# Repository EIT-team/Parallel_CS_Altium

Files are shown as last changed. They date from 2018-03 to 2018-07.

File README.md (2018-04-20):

# Parallel_CS_Altium

Altium files (root directory), fabrcation/assembly data and source code for UCL Parallel EIT Current Source.

### Fabrication_and_Assembly_Files
The most recently used Gerber files, BOM and Pick and Place data are included.

### src
Arduino source code for programming the CS. The latest board uses a 3.3V Arduino Pro Mini (ATMega328P).

### doc
Contains Circuit description, assembly instructions and operating instructions.

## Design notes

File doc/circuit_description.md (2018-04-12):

## Top level schematic
The design uses Altium's hierarchical sheet setup to replicate the CS block six times.
Additional sheets are used for the Power Supply/USB/Buttons and for the Arduino connector and clock source
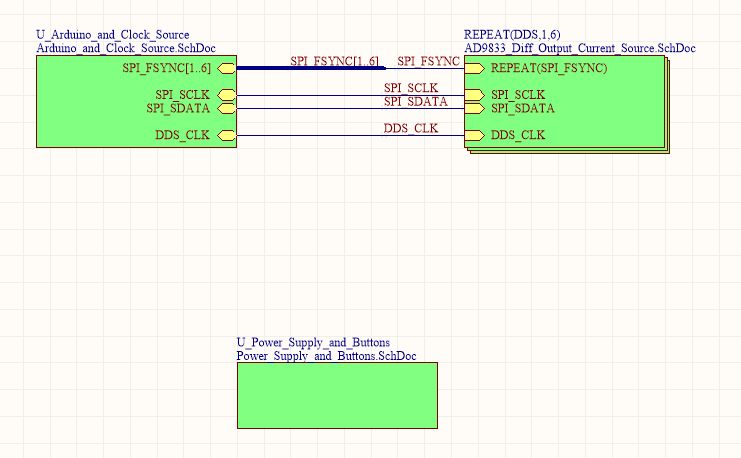
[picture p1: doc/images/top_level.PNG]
TOP


## Arduino Connector
A footprint for an Arduino Pro Micro/Pro Mini is included, which is used for sending SPI signals to the DDS chips. Each of the six current sources has its own FSYNC line.
The Arduino will need to be programmed once using the Arduino IDE, after which the frequencies are stored on board and it can be powered by the batery input.
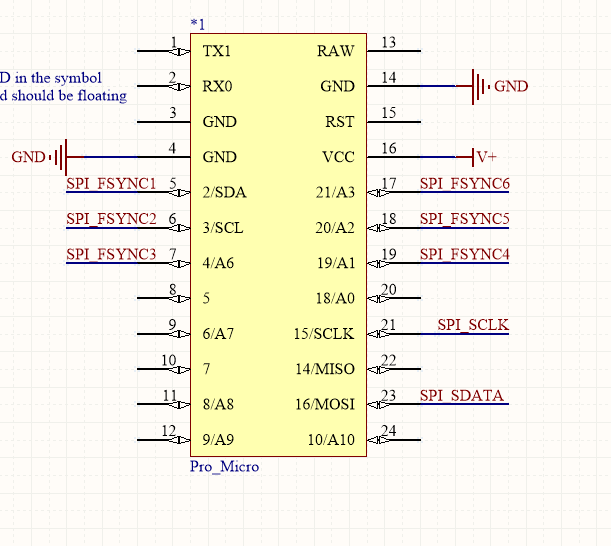
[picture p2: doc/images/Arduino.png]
ARDUINO


## Clock source
LTC6900 is used to generate a 10MHz clock signal for the DDS chips.  The clock speed is set by the resitor R17.
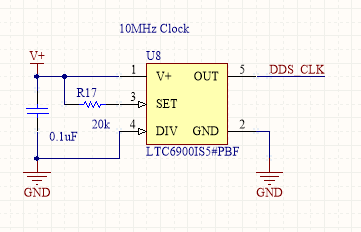
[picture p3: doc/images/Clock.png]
CLOCK


##Negate voltage generator
The op amps used in the single ended to differential convertor and the Howland Current Pump require a negative voltage. The LTC1044 generates this, from either the battery input or the USB line.
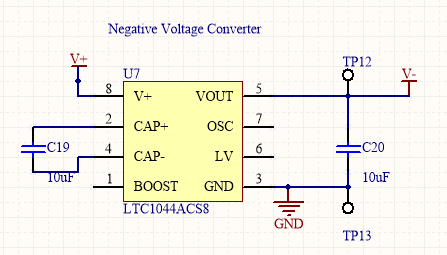
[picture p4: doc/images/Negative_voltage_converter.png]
VOLTAGE


## Battery and USB charger
Power can be supplied to the cirucit (including the Arduino) from a battery, or from the USB line. Switch S1 connects the battery, powering up the circuits. The on board LiPo charger can be used to charge the battery over USB.
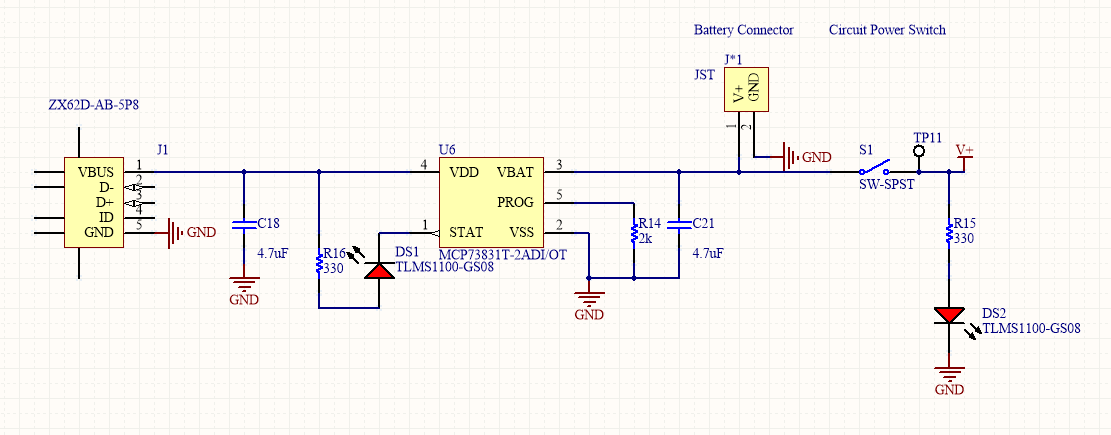
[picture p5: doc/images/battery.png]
BATTERY


## DDS and analog filter
AD9833 generates a 10-bit sine wave with 0.6V amplitude, the frequency is programmed over SPI from the Arduino. Op-amps U3A/U3B impement an image filter to reduce the higher frequency components on the sharp edges of the DDS signal.
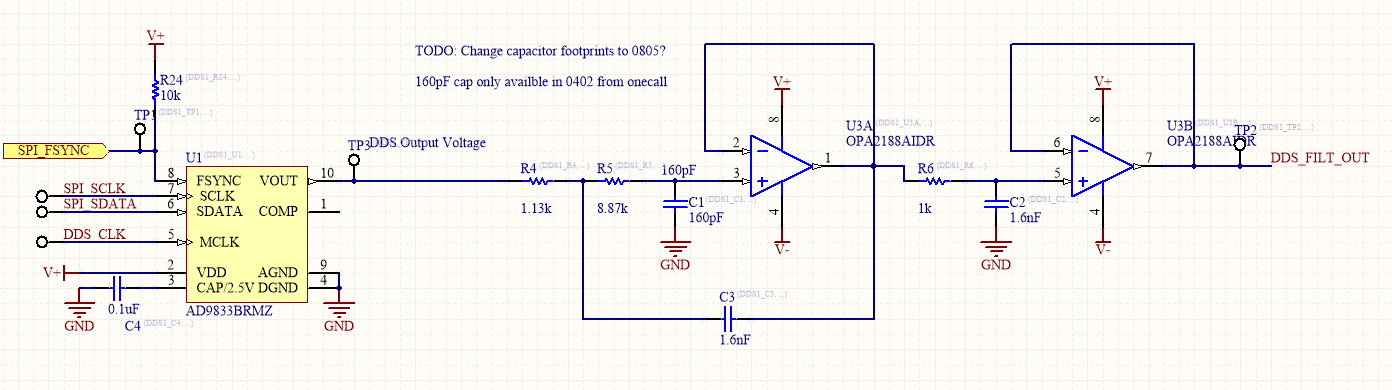
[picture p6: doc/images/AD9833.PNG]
DDS


## Single ended to differential conversion
The signal from the DDS/Filter block is single ended (reference to ground), but for parallel injection, differential signals are needed. These can be generated _either_ by the U9A/U9B op amp configuraiton _or_ the AD8476 IC. The AD8476 is a more expensive compoent, but is a simpler solution.
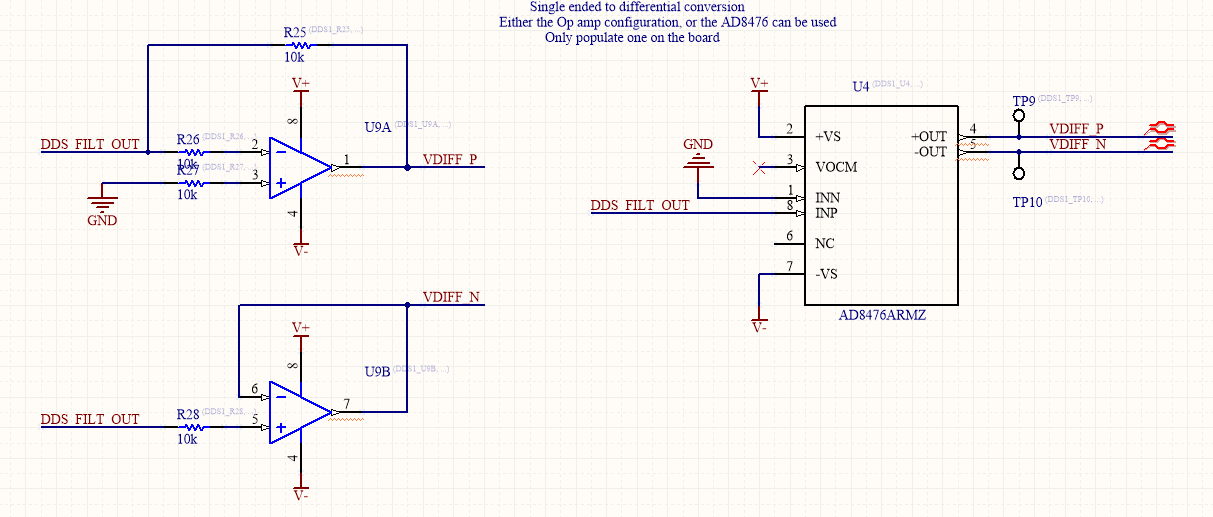
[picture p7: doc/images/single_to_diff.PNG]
DIFF


## Howland Current Pump
A differntial input Improved HCP circuit converts the DDS voltage signal to an output current. 4 output resistors are included to allow for selection of the output current, by using the header connections P2/P3 (both headers should be set to the same value).

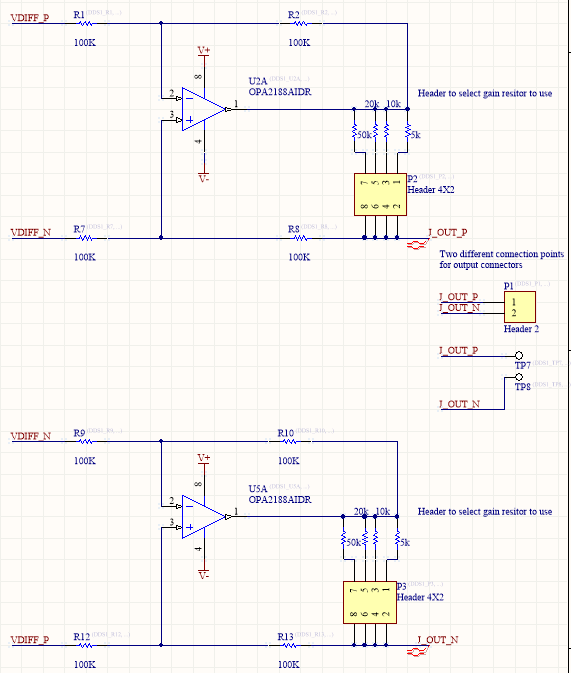
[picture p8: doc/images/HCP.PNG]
HCP


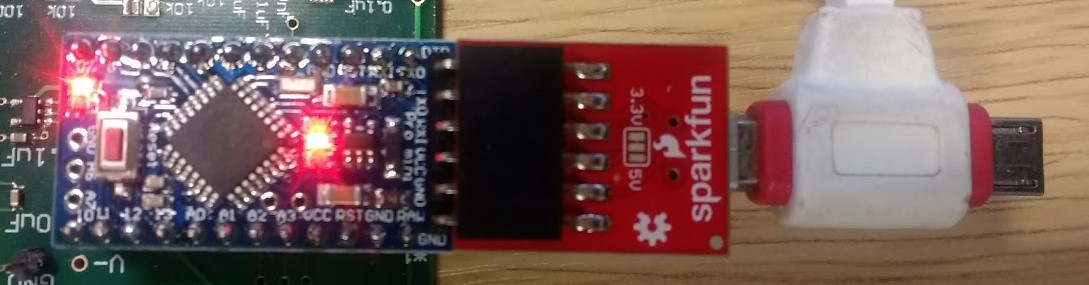
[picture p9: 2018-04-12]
doc/images/arduino-connected.jpg

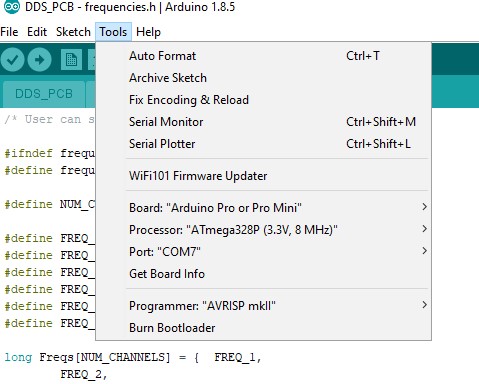
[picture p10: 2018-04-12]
doc/images/arduino-settings.jpg

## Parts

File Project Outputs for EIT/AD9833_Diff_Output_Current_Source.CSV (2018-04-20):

Bill of Material for
On 20/04/2018 at 06:43:15
Comment | Pattern | Quantity | Components
0.1uF | 1608[0603] | 73 | C22, DDS1_C4, DDS1_C5, DDS1_C6, DDS1_C7, DDS1_C8, DDS1_C9, DDS1_C10, DDS1_C12, DDS1_C14, DDS1_C16, DDS1_C23, DDS1_C24, DDS2_C4, DDS2_C5, DDS2_C6, DDS2_C7, DDS2_C8, DDS2_C9, DDS2_C10, DDS2_C12, DDS2_C14, DDS2_C16, DDS2_C23, DDS2_C24, DDS3_C4, DDS3_C5, DDS3_C6, DDS3_C7, DDS3_C8, DDS3_C9, DDS3_C10, DDS3_C12, DDS3_C14, DDS3_C16, DDS3_C23, DDS3_C24, DDS4_C4, DDS4_C5, DDS4_C6, DDS4_C7, DDS4_C8, DDS4_C9, DDS4_C10, DDS4_C12, DDS4_C14, DDS4_C16, DDS4_C23, DDS4_C24, DDS5_C4, DDS5_C5, DDS5_C6, DDS5_C7, DDS5_C8, DDS5_C9, DDS5_C10, DDS5_C12, DDS5_C14, DDS5_C16, DDS5_C23, DDS5_C24, DDS6_C4, DDS6_C5, DDS6_C6, DDS6_C7, DDS6_C8, DDS6_C9, DDS6_C10, DDS6_C12, DDS6_C14, DDS6_C16, DDS6_C23, DDS6_C24 | Capacitor (Semiconductor SIM Model)
100K | 6-0805_M | 48 | DDS1_R1, DDS1_R2, DDS1_R7, DDS1_R8, DDS1_R9, DDS1_R10, DDS1_R12, DDS1_R13, DDS2_R1, DDS2_R2, DDS2_R7, DDS2_R8, DDS2_R9, DDS2_R10, DDS2_R12, DDS2_R13, DDS3_R1, DDS3_R2, DDS3_R7, DDS3_R8, DDS3_R9, DDS3_R10, DDS3_R12, DDS3_R13, DDS4_R1, DDS4_R2, DDS4_R7, DDS4_R8, DDS4_R9, DDS4_R10, DDS4_R12, DDS4_R13, DDS5_R1, DDS5_R2, DDS5_R7, DDS5_R8, DDS5_R9, DDS5_R10, DDS5_R12, DDS5_R13, DDS6_R1, DDS6_R2, DDS6_R7, DDS6_R8, DDS6_R9, DDS6_R10, DDS6_R12, DDS6_R13 | Resistor
10k | 6-0805_M | 48 | DDS1_R6, DDS1_R18, DDS1_R21, DDS1_R24, DDS1_R25, DDS1_R26, DDS1_R27, DDS1_R28, DDS2_R6, DDS2_R18, DDS2_R21, DDS2_R24, DDS2_R25, DDS2_R26, DDS2_R27, DDS2_R28, DDS3_R6, DDS3_R18, DDS3_R21, DDS3_R24, DDS3_R25, DDS3_R26, DDS3_R27, DDS3_R28, DDS4_R6, DDS4_R18, DDS4_R21, DDS4_R24, DDS4_R25, DDS4_R26, DDS4_R27, DDS4_R28, DDS5_R6, DDS5_R18, DDS5_R21, DDS5_R24, DDS5_R25, DDS5_R26, DDS5_R27, DDS5_R28, DDS6_R6, DDS6_R18, DDS6_R21, DDS6_R24, DDS6_R25, DDS6_R26, DDS6_R27, DDS6_R28 | Resistor
10nF | 1608[0603] | 6 | DDS1_C11, DDS2_C11, DDS3_C11, DDS4_C11, DDS5_C11, DDS6_C11 | Capacitor (Semiconductor SIM Model)
10uF | 1608[0603] | 20 | C19, C20, DDS1_C13, DDS1_C15, DDS1_C17, DDS2_C13, DDS2_C15, DDS2_C17, DDS3_C13, DDS3_C15, DDS3_C17, DDS4_C13, DDS4_C15, DDS4_C17, DDS5_C13, DDS5_C15, DDS5_C17, DDS6_C13, DDS6_C15, DDS6_C17 | Capacitor (Semiconductor SIM Model)
13k | 6-0805_M | 6 | DDS1_R5, DDS2_R5, DDS3_R5, DDS4_R5, DDS5_R5, DDS6_R5 | Resistor
1u | 1608[0603] | 6 | DDS1_C2, DDS2_C2, DDS3_C2, DDS4_C2, DDS5_C2, DDS6_C2 | Capacitor (Semiconductor SIM Model)
2.2nF | 1608[0603] | 6 | DDS1_C3, DDS2_C3, DDS3_C3, DDS4_C3, DDS5_C3, DDS6_C3 | Capacitor (Semiconductor SIM Model)
20k | 6-0805_M | 13 | DDS1_R11, DDS1_R22, DDS2_R11, DDS2_R22, DDS3_R11, DDS3_R22, DDS4_R11, DDS4_R22, DDS5_R11, DDS5_R22, DDS6_R11, DDS6_R22, R17 | Resistor
220pF | 1608[0603] | 6 | DDS1_C1, DDS2_C1, DDS3_C1, DDS4_C1, DDS5_C1, DDS6_C1 | Capacitor (Semiconductor SIM Model)
2k | 6-0805_M | 1 | R14 | Resistor
330 | 6-0805_M | 2 | R15, R16 | Resistor
4.7uF | 1608[0603] | 2 | C18, C21 | Capacitor (Semiconductor SIM Model)
50k | 6-0805_M | 12 | DDS1_R3, DDS1_R23, DDS2_R3, DDS2_R23, DDS3_R3, DDS3_R23, DDS4_R3, DDS4_R23, DDS5_R3, DDS5_R23, DDS6_R3, DDS6_R23 | Resistor
5k | 6-0805_M | 12 | DDS1_R19, DDS1_R20, DDS2_R19, DDS2_R20, DDS3_R19, DDS3_R20, DDS4_R19, DDS4_R20, DDS5_R19, DDS5_R20, DDS6_R19, DDS6_R20 | Resistor
715 | 6-0805_M | 6 | DDS1_R4, DDS2_R4, DDS3_R4, DDS4_R4, DDS5_R4, DDS6_R4 | Resistor
AD8476ARMZ | SOP65P490X110-8N | 6 | DDS1_U4, DDS2_U4, DDS3_U4, DDS4_U4, DDS5_U4, DDS6_U4 | SP Amp DIFF AMP Single R-R O/P Â±9V/18V 8-Pin MSOP Tube
AD9833BRMZ | ADI-RM-10_M | 6 | DDS1_U1, DDS2_U1, DDS3_U1, DDS4_U1, DDS5_U1, DDS6_U1 | Low Power, 12.65 mW, 2.3 V to 5.5 V, Programmable Waveform Generator, 10-Bit, Serial, RM-10, 50 Tube, Pb-Free
Header 2 | HDR1X2 | 6 | DDS1_P1, DDS2_P1, DDS3_P1, DDS4_P1, DDS5_P1, DDS6_P1 | Header, 2-Pin
Header 4X2 | HDR2X4 | 12 | DDS1_P2, DDS1_P3, DDS2_P2, DDS2_P3, DDS3_P2, DDS3_P3, DDS4_P2, DDS4_P3, DDS5_P2, DDS5_P3, DDS6_P2, DDS6_P3 | Header, 4-Pin, Dual row
JST | JST- S2B-PH-SM4-TB(LF)(SN)-2_V | 1 | J*1
LTC1044ACS8 | LT-S8-8_M | 1 | U7 | 12 V CMOS Voltage Converter, 8-pin SOIC (S8-8), 0 to 70 degC
LTC6900IS5#PBF | LT-TSOT-23-5_V | 1 | U8 | Low Power, Resistor Set Oscillator, 1 KHz to 20 MHz, 2.7 to 5.5 V, -40 to 85 degC, 5-Pin SOT-23 (S5), Pb-Free
MCP73831T-2ADI/OT | SOT-23-OT5_M | 1 | U6 | Miniature Single-Cell, Fully Integrated Li-Ion, Li-Polymer Charge Management Controller, 4.2V, 5-Pin SOT-23, Industrial Temperature, Tape and Reel
OPA2188AIDR | D0008A_L | 24 | DDS1_U2, DDS1_U3, DDS1_U5, DDS1_U9, DDS2_U2, DDS2_U3, DDS2_U5, DDS2_U9, DDS3_U2, DDS3_U3, DDS3_U5, DDS3_U9, DDS4_U2, DDS4_U3, DDS4_U5, DDS4_U9, DDS5_U2, DDS5_U3, DDS5_U5, DDS5_U9, DDS6_U2, DDS6_U3, DDS6_U5, DDS6_U9 | 0.03 uV/degC, 6 uV Vos, Low Noise, Rail-to-Rail Output, Zero-Drift Operational Amplifier, 4 to 36 V, -40 to 105 degC, 8-pin SOIC (D8), Green (RoHS & no Sb/Br)
Pro_Micro | Pro_Micro | 1 | *1
SW-SPST | SPST-2 | 1 | S1 | Single-Pole, Single-Throw Switch
TESTPOINT_WHITE | TestPointVia | 63 | DDS1_TP1, DDS1_TP2, DDS1_TP3, DDS1_TP4, DDS1_TP5, DDS1_TP6, DDS1_TP7, DDS1_TP8, DDS1_TP9, DDS1_TP10, DDS2_TP1, DDS2_TP2, DDS2_TP3, DDS2_TP4, DDS2_TP5, DDS2_TP6, DDS2_TP7, DDS2_TP8, DDS2_TP9, DDS2_TP10, DDS3_TP1, DDS3_TP2, DDS3_TP3, DDS3_TP4, DDS3_TP5, DDS3_TP6, DDS3_TP7, DDS3_TP8, DDS3_TP9, DDS3_TP10, DDS4_TP1, DDS4_TP2, DDS4_TP3, DDS4_TP4, DDS4_TP5, DDS4_TP6, DDS4_TP7, DDS4_TP8, DDS4_TP9, DDS4_TP10, DDS5_TP1, DDS5_TP2, DDS5_TP3, DDS5_TP4, DDS5_TP5, DDS5_TP6, DDS5_TP7, DDS5_TP8, DDS5_TP9, DDS5_TP10, DDS6_TP1, DDS6_TP2, DDS6_TP3, DDS6_TP4, DDS6_TP5, DDS6_TP6, DDS6_TP7, DDS6_TP8, DDS6_TP9, DDS6_TP10, TP11, TP12, TP13
TLMS1100-GS08 | VISH-TLMX1100_V | 2 | DS1, DS2 | LED, RED, 2.1 V, -40 to 100 degC, 2-Pin SMD (0603), RoHS, Tape and Reel
ZX62D-AB-5P8 | HIRO-ZX62D-AB-5P8_V | 1 | J1 | USB 2.0 Standard Micro-USB Connector, Micro AB-Standard (Bottom Mount), 30 V AC, -30 to 85 degC, Right Angle, 5-Pin 7.5 x 5.6 x 2.8 mm SMD, RoHS, Reel

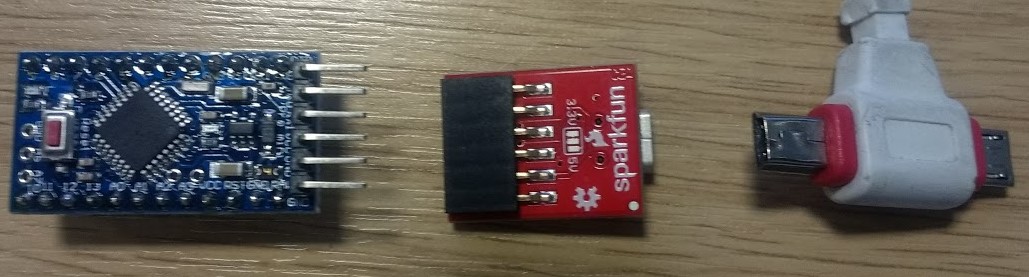
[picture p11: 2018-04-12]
doc/images/arduino-parts.jpg

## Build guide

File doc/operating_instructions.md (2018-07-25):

# Operating Instructions

### Programming the Arduino
Currently the board has a 3.3V Arduino Pro Micro.

The Pro Micro isn't included in the default set of Arduino boards. Follow the steps here to setup:

https://learn.sparkfun.com/tutorials/pro-micro--fio-v3-hookup-guide/installing-windows#windows_boardaddon

Once connected, open the Adruino code from the _src/DUE_DAC_ folder. The operating frequencies of the 6 current sources can be set by editing _frequencies.h_.

**Upload settings**

If the boards have been updated successfully, select Tools->Boards->Sparkfun Pro Micro.

Once programmed, the usb lead is no longer needed and can be disconected.

<br><br>

### Setting output current
The banks of 2x4 headers on the board are used to set the output current, by connecting a jumper between sets of pins.

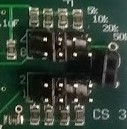
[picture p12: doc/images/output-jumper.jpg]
HEADERS


The values of gain resistor on the board are 50k (12uA) , 20k (30uA), 10k (60uA) and 5k (120uA), but these could be replaced if different values are needed. 

**NOTE: The silkscreen text is the wrong way round! The leftmost set of jumpers is the lowest current, and the rightmost is the highest**

Each CS has two sets of headers (there are two op amps used in the output stage), which should be set to the same value.

<br><br>

### Starting stimulation

**Conenct output leads and 3.7V LiPo battery**

**Start/stop stimulation with push button**

The push button turns on/off power to the Arduino and current sources. Assuming the Arduino has been programmed, once powered up the CS should start outputting after a few seconds.

<br><br>

### Charging battery
There is a LiPo charging circuit built into the board. Attaching a USB Micro lead will charge a connected battery.

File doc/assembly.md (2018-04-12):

# Final Assembly Steps

The assembly files included in _../Fabrication_and_Assembly_Files_ are populated with nearly all of the compoents for the full board.
A few additional components need to be hand soldered (or added to the pick and place data).

### Board as recieved from PCB Assembly House
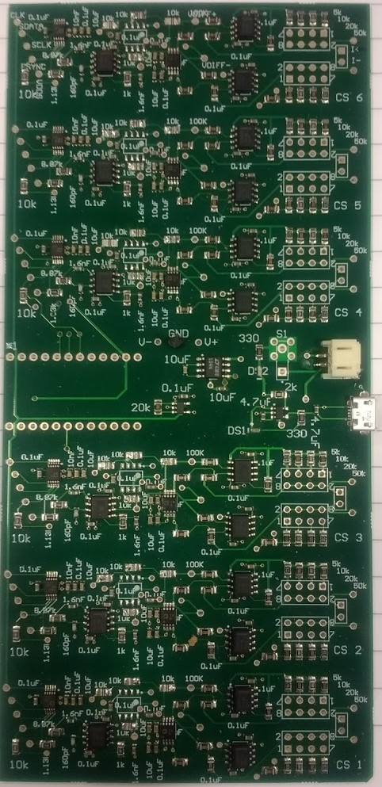
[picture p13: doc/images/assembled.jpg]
PCB_Board


#### Add 8-way headers
The header pins (Farnell item 1593441), used to select the output current, need to be soldered into these spaces:

header_slot

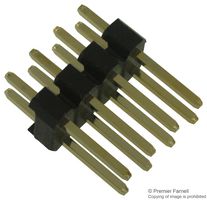
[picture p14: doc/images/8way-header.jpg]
header


#### Output connectors
Output connectors (2.54mm pitch) can be soldered into:

outputs

#### Arduino socket
2 rows of 12 pins (2.54mm pitch) need to be soldered in to allow the Arduino to connect. Any standard 2.54mm socket should be fine. The Arduino could be soldered directly in, but if it becomes damaged, it will be difficult to replace. 

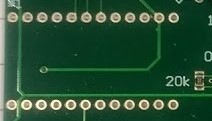
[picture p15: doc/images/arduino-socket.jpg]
arduino_slot


#### On/off switch

I used a stock Altium footprint for a switch, but haven't found a suitable switch which matches (I'm sure one will be available from Farnell). In the meantime, I used a 4 pin switch we already had (Farnell 2435325) and snipped off 2 of the legs to fit it in.

switch_slot

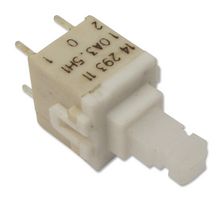
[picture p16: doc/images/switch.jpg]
switch


### Finished board
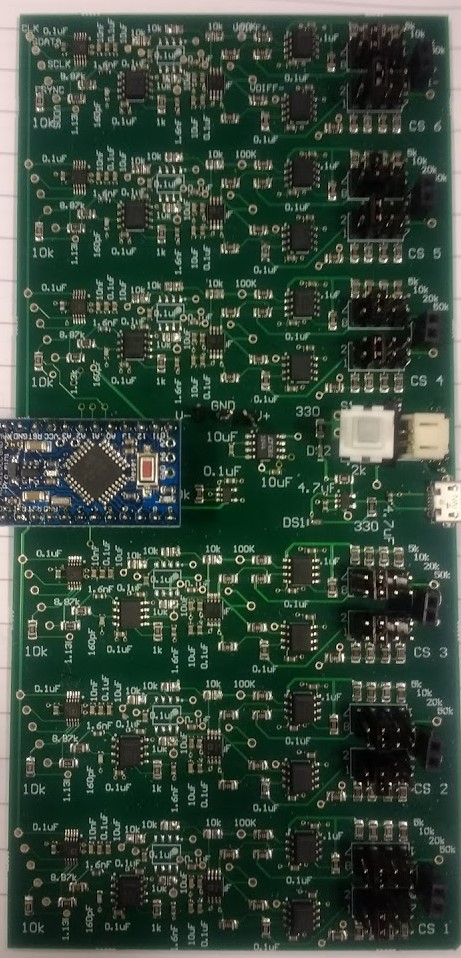
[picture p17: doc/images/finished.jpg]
Finished_Board


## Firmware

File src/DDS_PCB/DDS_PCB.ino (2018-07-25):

// Library for handling the SPI transfer
#include <SPI.h>

#include "definitions.h"
#include "frequencies.h"
#include <stdio.h>

void setup() {

  Serial.begin(SERIAL_BAUD_RATE);

  pinMode(FSYNC1_Pin, OUTPUT);
  pinMode(FSYNC2_Pin, OUTPUT);
  pinMode(FSYNC3_Pin, OUTPUT);
  pinMode(FSYNC4_Pin, OUTPUT);
  pinMode(FSYNC5_Pin, OUTPUT);
  pinMode(FSYNC6_Pin, OUTPUT);

    //Set FSYNC pins High. FSYNC is active low
  digitalWrite(FSYNC1_Pin, HIGH); 
  digitalWrite(FSYNC2_Pin, HIGH); 
  digitalWrite(FSYNC3_Pin, HIGH);
  digitalWrite(FSYNC4_Pin, HIGH); 
  digitalWrite(FSYNC5_Pin, HIGH); 
  digitalWrite(FSYNC6_Pin, HIGH); 

  // For SPI data transfer setup
  pinMode(SDATA_SPI_Pin, OUTPUT);
  pinMode(SCLK_SPI_Pin, OUTPUT);

  digitalWrite(SDATA_SPI_Pin, LOW);
  digitalWrite(SCLK_SPI_Pin, LOW);

  // Arduino handles most of the underlying SPI transfer by itself, set it up here
  SPI.begin();  // Enable SPI
  SPI.setBitOrder(MSBFIRST);  // Send data Most significant bit first, this is necessary for the AD9833
  SPI.setDataMode(SPI_MODE2);  // Set SPI Mode 2 (Data captured on falling edge of clock, clock inversion on)
  SPI.setClockDivider(SPI_CLOCK_DIV128);    // Set clock divider (optional)
}

void loop() {

  byte byteRead; // Serial read data
  int val_to_program; // Frequency (Hz), phase (degrees), time etc.
  int chan_to_program;
  String what_to_program; //  Command to execute

  // Allow setting of frequency/phase from serial monitor
  // Input 'freq val_to_program' to program frequency
  // 'phase val_to_program' to set phase
    delay(ONE_SECOND_DELAY);
    if (PROGRAM_ALL) {
      Program_Freqs(Freqs, NUM_CHANNELS);
    }

    else {
      Program_One_Frequency(Freqs, CHANNEL_TO_PROGRAM);  
    }
    
  while (1) {
    // Wait for Serial data to be received and parse it


    
    if (Serial.available()) {

      what_to_program = Serial.readStringUntil(' '); // Get a string
      val_to_program = Serial.parseInt(); // Get an int
      chan_to_program = Serial.parseInt();

      // Process input and call appropriate commands
      // Can't use switch statement to do this as it won't accept a string as a comparator
      if (what_to_program == "reset")  {
        Reset_DDS(chan_to_program);
      }

      else if (what_to_program == "freq")     {
        Set_AD9833_Frequency(val_to_program, chan_to_program);
      }

      else if (what_to_program == "phase")	 {
        Set_AD9833_Phase(val_to_program, chan_to_program);
      }

      // default case - invalid command has been passed
      else {
        Serial.println("Command not recognised.");
      }
    }
  }
}


// Additional functions that may be helpful

void Program_Freqs (long Freqs [], int n_chans) {
  
  /* Loop through each freq/chan pair and program the switches/DDS chip */

  Serial.println("Programming default frequencies");
  for (int i = 0; i < n_chans; i++) {
    Serial.print("Programming channel ");
    Serial.println(i);
    Set_AD9833_Frequency(Freqs[i], i + 1);
  }
}

void Program_Then_Turn_Off(long freq, unsigned int on_time_milli, int chan) {

  /*Program the DDS chip for a given time, then turn off */

  //Program all of the channels, wait a specified time, then turn off.
  Set_AD9833_Frequency(freq, chan);
  delay(on_time_milli);
  Reset_DDS(chan);

}

void Program_One_Frequency(long Freqs [], int chan_to_turn_on) {
  /* Only program one current source, set all the rest to off/midscale DC output */

  Serial.print("Programming only source ");
  Serial.println(chan_to_turn_on);

  Reset_All();
  delay(100);
  Set_AD9833_Frequency(Freqs[chan_to_turn_on], chan_to_turn_on);    

}

void Sweep_Freq (int freq_min, int freq_step, int freq_max, int on_time, int chan) {
  /* Sweeps the frequency output on a channel, with increment and max value set by user.
freq_min: starting frequency (Hz)
freq_step: increment (Hz)
freq_max: Stopping frequency (Hz)
chan: which channel to program
on_time: how long to program each channel for (milliseconds) */

  for (int i = freq_min ; i <= freq_max; i = i + freq_step) {
    Set_AD9833_Frequency(i, chan);
    delay(on_time);
  }
}


void Reset_DDS(int chan) {
  /* Reset channel to midscale output (turns off AC output) */
  AD9833_SendWord(RESET_CONTROL_REGISTER, chan);
}


void Reset_All() {
  for (int i = 0; i < NUM_CHANNELS; i++) {
    Reset_DDS(i);
  }
 
}

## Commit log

2017-11-15 First commit, about to do final route for PCB
    [AD9833_Diff_Output_Current_Source.SchDoc, Arduino_and_Clock_Source.SchDoc, EIT.PrjPcb, HCP_Single_Ended.SchDoc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]
2017-11-16 Single channel layout done, starting whole board
    [AD9833_Diff_Output_Current_Source.SchDoc, Arduino_and_Clock_Source.SchDoc, Power_Supply_and_Buttons.SchDoc]
2017-11-16 Whole board routing done, starting silkscreen placement
    [EIT.PrjPcb, Parallel_CS.PcbDoc]
2018-02-02 2nd Feb 2018.
    [AD9833_Diff_Output_Current_Source.SchDoc, AD9833_Single_Ended.SchDoc, Arduino_and_Clock_Source.SchDoc, EIT.PrjPcb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]
2018-02-06 Removed unwanted files
    [AD9833_Single_Ended.SchDoc, adg731-switches.SchDoc]
2018-02-06 Fixed problem with power supply schematic being shared with another project
    [Parallel_CS.PcbDoc, Power_Supply_and_Buttons.SchDoc]
2018-02-06 Fixed wrong connection on HCP, added pullups on FSYNC
    [AD9833_Diff_Output_Current_Source.SchDoc, Arduino_and_Clock_Source.SchDoc, Parallel_CS.PcbDoc, Power_Supply_and_Buttons.SchDoc]
2018-03-02 Added circuit description
2018-03-15 Integrated library
    [AD9833_Diff_Output_Current_Source.SchDoc, EIT.PrjPcb, Parallel_CS.PcbDoc, Power_Supply_and_Buttons.SchDoc]
2018-04-12 Added Arduino code to same repo as schematics
2018-04-12 Added fabrication and assembly files
2018-04-12 Added assembly images
2018-04-12 More images for assembly
2018-04-12 Adruion socket image
2018-04-18 fixing bugs 18/04/18
    [AD9833_Diff_Output_Current_Source.SchDoc, Parallel_CS.PcbDoc]
2018-04-20 Board complete April 2018
    [AD9833_Diff_Output_Current_Source.SchDoc, Parallel_CS.PcbDoc]
2018-04-20 Updated design to include DC offset removal, BOM to use op-amp for Diff signal generation
    [AD9833_Diff_Output_Current_Source.CSV, AD9833_Diff_Output_Current_Source.SchDoc, AD9833_Diff_Output_Current_Source.sch, Arduino_and_Clock_Source.sch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]
2018-04-24 Added outline layer to Gerbers at request of PCBTrain
    [Parallel_CS.GBL, Parallel_CS.GKO, Parallel_CS.GTL, Parallel_CS.GTO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]
2018-07-25 Changed pinout for Pro Micro board
